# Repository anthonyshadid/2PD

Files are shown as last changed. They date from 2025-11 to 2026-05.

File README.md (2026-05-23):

# 2PD Generator

Tools for generating 3D-printable two-point discrimination wheels. Available as a web app and a native iOS app.

---

## Website

A Flask web app deployed via Docker on Render. Users can download preset STL wheels or enter 8 custom distances to generate a wheel on the server using OpenSCAD.

**Live at:** [https://anthonyshadid.github.io/2PD](https://anthonyshadid.github.io/2PD)

### How It Works

1. User enters 8 distances (0-17 mm) in the browser.
2. The server runs OpenSCAD with those distances as parameters against `discriminator.scad`.
3. The generated STL is returned as a file download.

Preset STL files (fine and broad) are served directly as static assets.

### Stack

- Python / Flask
- OpenSCAD (headless, via `xvfb-run` in the container)
- Docker, deployed on Render

### Running Locally

```bash
pip install -r requirements.txt
python app.py
```

The app starts on port 5000 by default. OpenSCAD must be installed and on your PATH.

### Running with Docker

```bash
docker build -t 2pd .
docker run -p 5000:5000 2pd
```

### Project Structure

```
app.py               Flask routes
make_wheel.py        Calls OpenSCAD to produce STL output
discriminator.scad   Parametric wheel model
templates/           HTML templates
static/presets/      Pre-built STL files
Dockerfile
render.yaml
```

### Deployment

The app deploys automatically on push to main via `render.yaml`. No manual steps needed.

---

## iPhone App

A native iOS app that generates STL files entirely on-device, no server or OpenSCAD required. The geometry is reimplemented in Swift using the same parameters as `discriminator.scad`.

**App Store:** [2PD on the App Store](https://apps.apple.com/us/app/2pd/id6761318358)

### How It Works

1. User enters up to 8 distances in the app.
2. `SCADCompatModeler.swift` computes the wheel geometry and writes an STL file.
3. The standard iOS share sheet lets the user save to Files, AirDrop, or open in a slicer app.

All processing is on-device. No network connection needed.

### Stack

- Swift / SwiftUI
- Xcode
- No third-party dependencies

### Project Structure

```
2PDiPhone/
  2PDiPhone/
    TwoPDApp.swift          App entry point, tab structure
    ContentView.swift       Distance input form and STL export
    AboutView.swift         About and usage information
    SCADCompatModeler.swift On-device STL geometry engine
    Assets.xcassets/        App icon and colors
  2PDiPhone.xcodeproj/
```

### Building

Open `2PDiPhone/2PDiPhone.xcodeproj` in Xcode and run on a simulator or device. No additional setup required.

### Modeler Parameters

The on-device modeler matches the SCAD defaults:

| Parameter | Value |
|---|---|
| Wheel diameter (flat-to-flat) | 40 mm |
| Body thickness | 3 mm |
| Prong length | 7 mm |
| Prong thickness | 1.4 mm |
| Hub diameter | 17 mm |
| Lanyard hole | 3.5 mm diameter, at corner |

---

## Contributing

Bug reports and pull requests welcome. The SCAD file and the Swift modeler should stay in sync; if you change `discriminator.scad` geometry, update `SCADCompatModeler.swift` to match.

## Authors

Anthony Shadid and Keyvon Rashidi

## License

Open source. See LICENSE for details.

## Disclaimer

Not for diagnostic use unless validated and approved by your institution. Provided as-is without warranties of any kind.

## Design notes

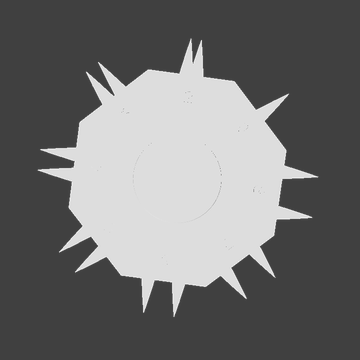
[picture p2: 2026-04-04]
static/2pd_spin.png

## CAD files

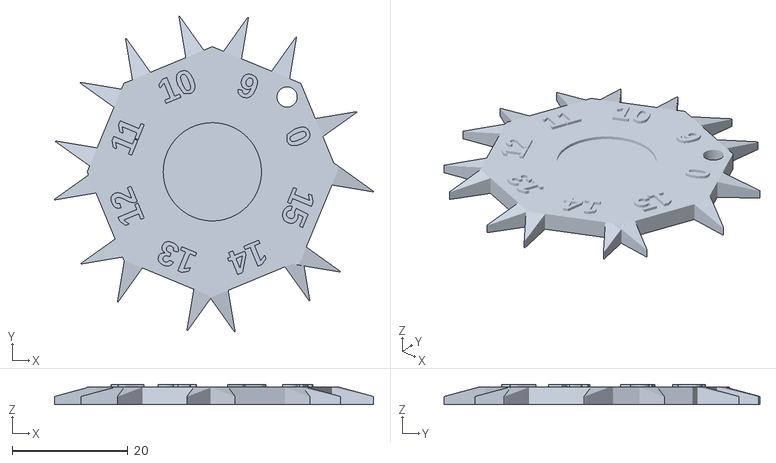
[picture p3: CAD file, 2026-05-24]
static/presets/attachables/broad_preset6 keyhole.stl
55.2 x 54.6 x 3.49

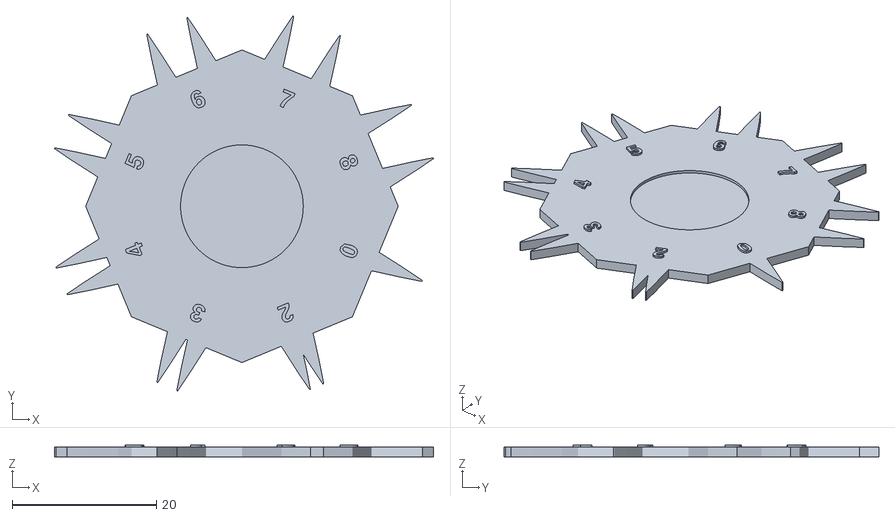
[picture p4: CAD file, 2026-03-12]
static/presets/fine_preset3.stl
52.5 x 51.9 x 1.69

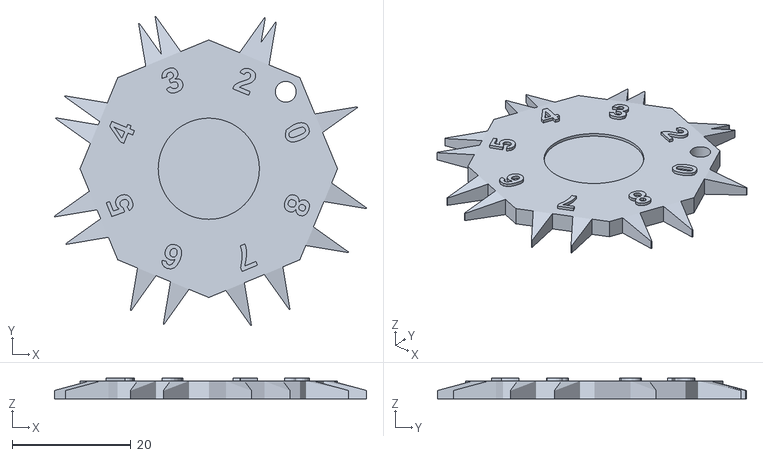
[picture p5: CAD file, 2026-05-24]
static/presets/attachables/fine_preset6 keyhole.stl
52.5 x 51.9 x 3.49

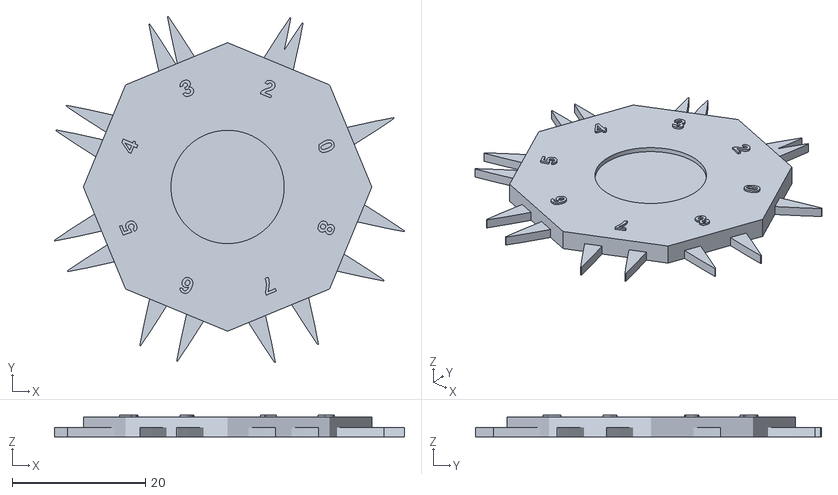
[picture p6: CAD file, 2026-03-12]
static/presets/fine_preset4.stl
52.5 x 51.9 x 3.29

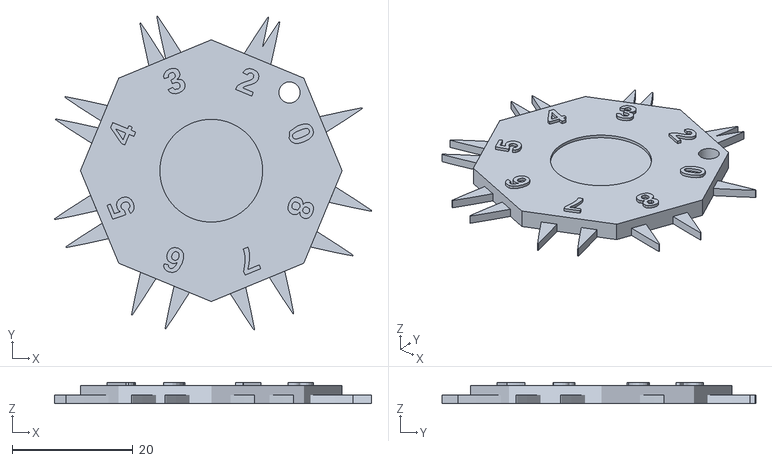
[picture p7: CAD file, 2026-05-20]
static/presets/attachables/fine_preset5 keyhole.stl
52.5 x 51.9 x 3.49

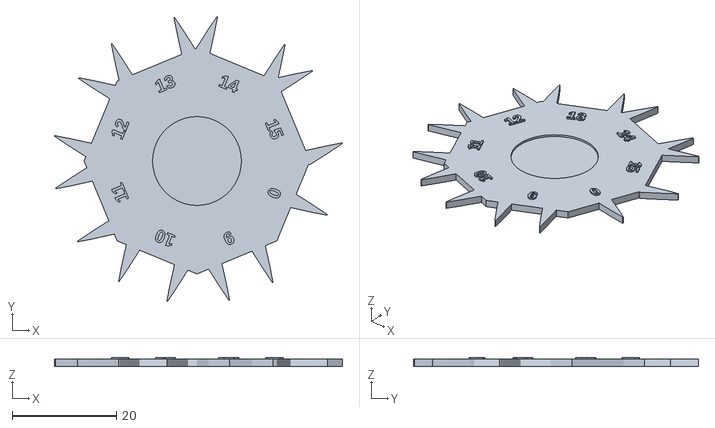
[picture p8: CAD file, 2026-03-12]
static/presets/broad_preset3.stl
55.2 x 54.6 x 1.69

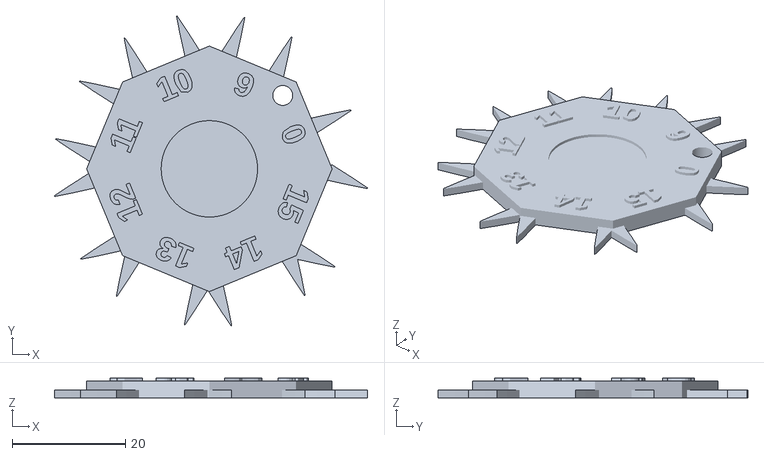
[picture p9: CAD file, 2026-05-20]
static/presets/attachables/broad_preset5 keyhole.stl
55.2 x 54.6 x 3.49

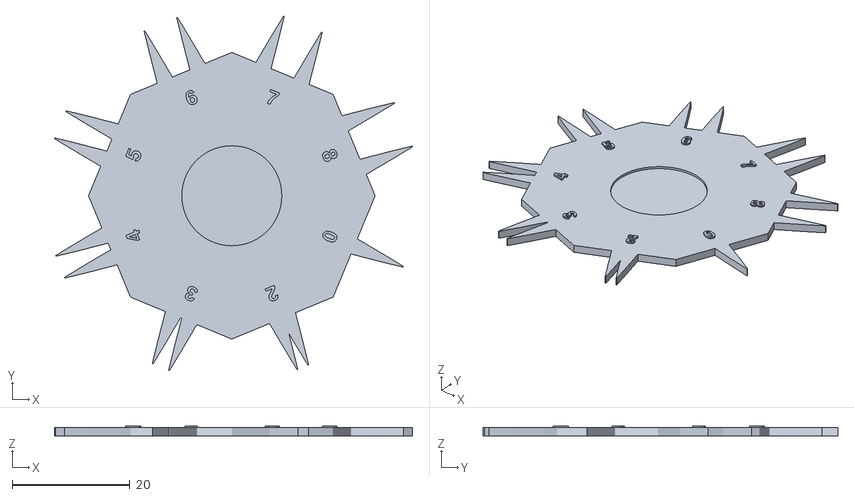
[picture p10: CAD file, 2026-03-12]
static/presets/fine_preset2.stl
60.8 x 60.3 x 1.69

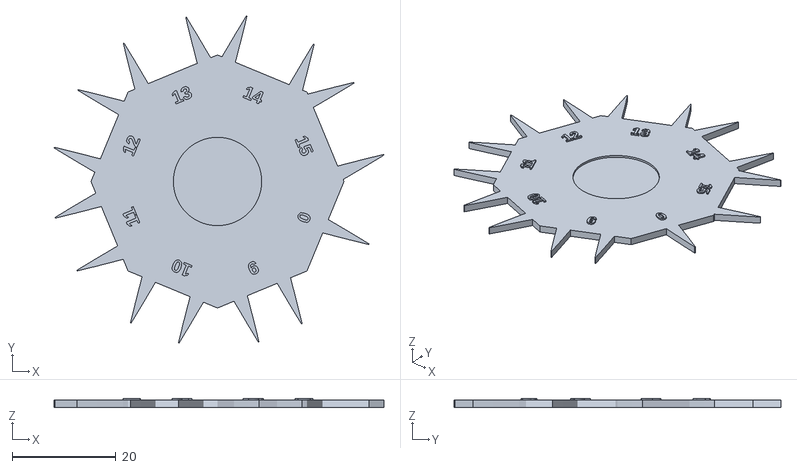
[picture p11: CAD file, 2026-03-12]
static/presets/broad_preset2.stl
63.5 x 62.9 x 1.69

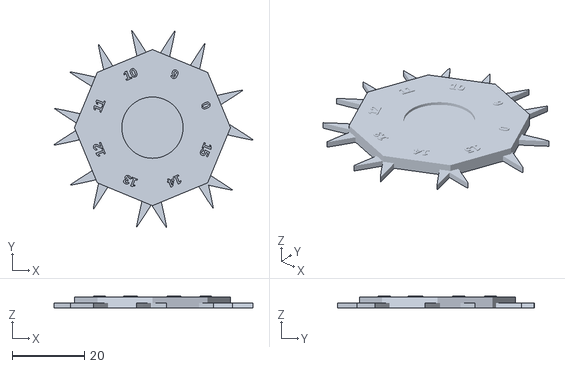
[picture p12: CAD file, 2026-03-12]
static/presets/broad_preset4.stl
55.2 x 54.6 x 3.29

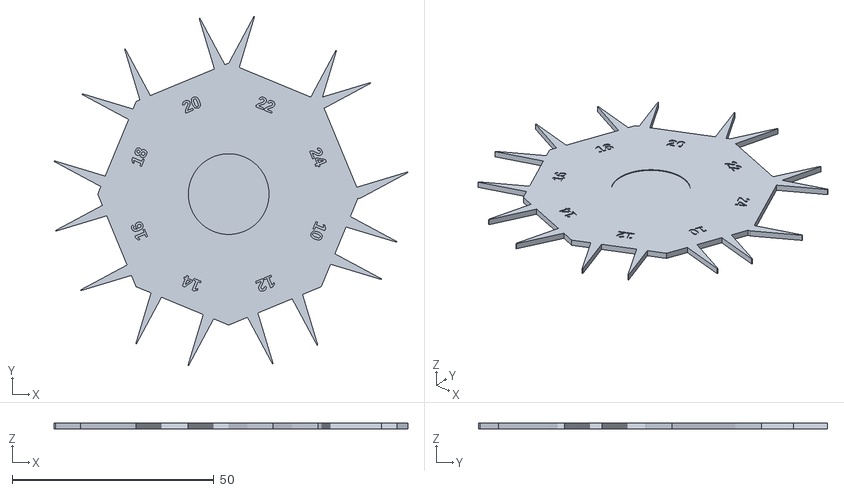
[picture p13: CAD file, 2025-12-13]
static/presets/broad_preset.stl
87.7 x 86.5 x 1.50

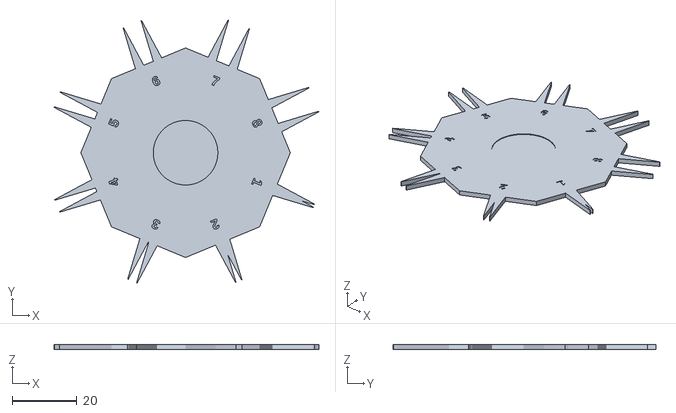
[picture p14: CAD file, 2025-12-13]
static/presets/fine_preset.stl
82.1 x 81.6 x 1.50

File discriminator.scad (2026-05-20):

// 2-Point Discrimination Wheel — parametric n-gon, COUNTERclockwise order + split thickness
// Includes badge/lanyard through-hole between 0 mm and 2 mm

distances_mm       = is_undef(distances_mm) ? [0,2,3,4,5,6,7,8] : distances_mm;

// --- geometry ---
outer_flat_to_flat = is_undef(outer_flat_to_flat) ? 40 : outer_flat_to_flat;
body_thickness     = is_undef(body_thickness) ? 3 : body_thickness;
prong_thickness    = is_undef(prong_thickness) ? 1.4 : prong_thickness;

spike_length  = is_undef(spike_length) ? 7 : spike_length;
base_d        = is_undef(base_d) ? 3 : base_d;
shank_d       = is_undef(shank_d) ? 1.4 : shank_d;
tip_d         = is_undef(tip_d) ? 0.15 : tip_d;
root_overlap  = is_undef(root_overlap) ? .7 : root_overlap;

// --- labels / hub ---
label_size    = is_undef(label_size) ? 4.3 : label_size;
label_depth   = is_undef(label_depth) ? .5 : label_depth;
font_name     = is_undef(font_name) ? "Liberation Sans:style=Bold" : font_name;
label_radial  = is_undef(label_radial) ? 0.80 : label_radial;
hub_diameter  = is_undef(hub_diameter) ? 17 : hub_diameter;
thumb_depth   = is_undef(thumb_depth) ? .5 : thumb_depth;

// --- lanyard / badge hole ---
lanyard_hole_d      = is_undef(lanyard_hole_d) ? 3.5 : lanyard_hole_d;
lanyard_hole_inset  = is_undef(lanyard_hole_inset) ? 3.35 : lanyard_hole_inset;
// larger inset = farther inward from the octagon corner
// 5.0 should place it slightly inside the corner between 0 and 2 mm

// optional
chamfer = is_undef(chamfer) ? 0.8 : chamfer;
$fn = is_undef($fn) ? 72 : $fn;

function apothem(across_flats,n)=across_flats/2;
function circ_radius(across_flats,n)=across_flats/(2*cos(180/n));

// Use BODY thickness for anything “top referenced”
function total_thickness()=body_thickness + max(chamfer,0);

module polygon_plate(n, across_flats, thk){
  r = circ_radius(across_flats,n);
  linear_extrude(thk)
    polygon(points=[for(i=[0:n-1]) let(a=360*i/n)[r*cos(a), r*sin(a)]]);
}

module spike_single_flat(len=spike_length,bd=base_d,sd=shank_d,td=tip_d){
  base_r=bd/2; shank_r=sd/2; tip_r=td/2;
  bx=-root_overlap; sx=len*0.55; tx=len;

  linear_extrude(height=prong_thickness)
  union(){
    translate([bx,0]) circle(r=base_r);
    hull(){
      translate([bx,0]) circle(r=base_r);
      translate([sx,0]) circle(r=shank_r);
    }
    hull(){
      translate([sx,0]) circle(r=shank_r);
      translate([tx,0]) circle(r=tip_r);
    }
  }
}

module thumb_well_top(){
  translate([0,0,body_thickness - thumb_depth])
    cylinder(h=thumb_depth,d=hub_diameter,$fn=72);
}

module lanyard_corner_hole(distances){
  n = len(distances);
  R = circ_radius(outer_flat_to_flat,n);

  // For default [0,2,3,4,5,6,7,8]:
  // distance[0] is at 22.5 degrees, distance[1] is at 67.5 degrees,
  // so the corner between 0 and 2 mm is at 45 degrees.
  ang = 360 / n;

  translate([(R - lanyard_hole_inset) * cos(ang),
             (R - lanyard_hole_inset) * sin(ang),
             -0.1])
    cylinder(h = body_thickness + 0.2, d = lanyard_hole_d, $fn = 72);
}

module edge_numbers_top(distances,a){
  n=len(distances);
  for(i=[0:n-1]){
    angN=+360*(i+0.5)/n;

    translate([(label_radial*a)*cos(angN),
               (label_radial*a)*sin(angN),
               body_thickness - 0.01])
      rotate([0,0,angN-90])
        linear_extrude(height=label_depth)
          text(str(distances[i]),
               size=label_size,font=font_name,
               halign="center",valign="center");
  }
}

module wheel_solid(distances){
  n=len(distances);
  a=apothem(outer_flat_to_flat,n);

  union(){
    polygon_plate(n,outer_flat_to_flat,body_thickness);

    for(i=[0:n-1]){
      angN=+360*(i+0.5)/n;

      translate([a*cos(angN),a*sin(angN),0])
        rotate([0,0,angN]){
          sep=distances[i];
          translate([0,+sep/2,0]) spike_single_flat();
          translate([0,-sep/2,0]) spike_single_flat();
        }
    }
  }
}

module discriminator(distances){
  n=len(distances);
  assert(n>=3,"distances_mm must have at least 3 entries.");

  union(){
    difference(){
      wheel_solid(distances);
      thumb_well_top();
      lanyard_corner_hole(distances);
    }

    edge_numbers_top(distances, apothem(outer_flat_to_flat,n));
  }
}
discriminator(distances_mm);

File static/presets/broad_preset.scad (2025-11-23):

// 2-Point Discrimination Wheel — parametric n-gon, clockwise order
distances_mm       = is_undef(distances_mm) ? [5,8,10,12,15,20,25,30] : distances_mm;
outer_flat_to_flat = is_undef(outer_flat_to_flat) ? 63.5 : outer_flat_to_flat;
base_thickness     = is_undef(base_thickness) ? 3.0 : base_thickness;
spike_length  = is_undef(spike_length) ? 14 : spike_length;
base_d        = is_undef(base_d) ? 3 : base_d;
shank_d       = is_undef(shank_d) ? 1.4 : shank_d;
tip_d         = is_undef(tip_d) ? 0.6 : tip_d;
root_overlap  = is_undef(root_overlap) ? 0.7 : root_overlap;
label_size    = is_undef(label_size) ? 3 : label_size;
label_depth   = is_undef(label_depth) ? 0.5 : label_depth;
font_name     = is_undef(font_name) ? "DejaVu Sans:style=Bold" : font_name;
label_radial  = is_undef(label_radial) ? 0.80 : label_radial;
hub_diameter  = is_undef(hub_diameter) ? 20 : hub_diameter;
thumb_depth   = is_undef(thumb_depth) ? 0.5 : thumb_depth;
chamfer = is_undef(chamfer) ? 0.8 : chamfer;
$fn = is_undef($fn) ? 72 : $fn;

module soft_chamfer(h=chamfer){
  if (h>0) minkowski(){ children(); cylinder(h=h,r1=h,r2=0,$fn=24); }
  else children();
}
function apothem(across_flats,n)=across_flats/2;
function circ_radius(across_flats,n)=across_flats/(2*cos(180/n));
function total_thickness()=base_thickness+max(chamfer,0);

module polygon_plate(n, across_flats, thk){
  r=circ_radius(across_flats,n);
  soft_chamfer()
    linear_extrude(thk)
      polygon(points=[for(i=[0:n-1]) let(a=360*i/n)[r*cos(a),r*sin(a)]]);
}

module spike_single_flat(len=spike_length,bd=base_d,sd=shank_d,td=tip_d){
  base_r=bd/2; shank_r=sd/2; tip_r=td/2;
  bx=-root_overlap; sx=len*0.55; tx=len;
  linear_extrude(height=base_thickness)
  union(){
    translate([bx,0]) circle(r=base_r);
    hull(){translate([bx,0])circle(r=base_r);translate([sx,0])circle(r=shank_r);}
    hull(){translate([sx,0])circle(r=shank_r);translate([tx,0])circle(r=tip_r);}
  }
}

module thumb_well_top(){
  translate([0,0,total_thickness()-thumb_depth])
    cylinder(h=thumb_depth,d=hub_diameter,$fn=72);
}

module edge_numbers_top(distances,a){
  n=len(distances);
  for(i=[0:n-1]){
    angN=-360*(i+0.5)/n;
    translate([(label_radial*a)*cos(angN),
               (label_radial*a)*sin(angN),
               total_thickness()-label_depth])
      rotate([0,0,angN-90])
        linear_extrude(height=label_depth)
          text(str(distances[i]),
               size=label_size,font=font_name,
               halign="center",valign="center");
  }
}

module wheel_solid(distances){
  n=len(distances);
  a=apothem(outer_flat_to_flat,n);
  union(){
    polygon_plate(n,outer_flat_to_flat,base_thickness);
    for(i=[0:n-1]){
      angN=-360*(i+0.5)/n;
      translate([a*cos(angN),a*sin(angN),0])
        rotate([0,0,angN]){
          sep=distances[i];
          translate([0,+sep/2,0])spike_single_flat();
          translate([0,-sep/2,0])spike_single_flat();
        }
    }
  }
}

module discriminator(distances){
  n=len(distances);
  assert(n>=3,"distances_mm must have at least 3 entries.");
  difference(){
    wheel_solid(distances);
    thumb_well_top();
    edge_numbers_top(distances,apothem(outer_flat_to_flat,n));
  }
}

discriminator(distances_mm);

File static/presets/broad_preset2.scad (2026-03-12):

// 2-Point Discrimination Wheel — parametric n-gon, clockwise order
distances_mm       = is_undef(distances_mm) ? [0,9,10,11,12,13,14,15] : distances_mm;
outer_flat_to_flat = is_undef(outer_flat_to_flat) ? 45 : outer_flat_to_flat;
base_thickness     = is_undef(base_thickness) ? 1.4 : base_thickness;
spike_length  = is_undef(spike_length) ? 9 : spike_length;
base_d        = is_undef(base_d) ? 3 : base_d;
shank_d       = is_undef(shank_d) ? 1.4 : shank_d;
tip_d         = is_undef(tip_d) ? 0.15 : tip_d;
root_overlap  = is_undef(root_overlap) ? .7 : root_overlap;
label_size    = is_undef(label_size) ? 2.5 : label_size;
label_depth   = is_undef(label_depth) ? .3 : label_depth;
font_name     = is_undef(font_name) ? "DejaVu Sans:style=Bold" : font_name;
label_radial  = is_undef(label_radial) ? 0.80 : label_radial;
hub_diameter  = is_undef(hub_diameter) ? 17 : hub_diameter;
thumb_depth   = is_undef(thumb_depth) ? 1.2 : thumb_depth;
chamfer = is_undef(chamfer) ? 0.8 : chamfer;
$fn = is_undef($fn) ? 72 : $fn;

module soft_chamfer(h=chamfer){
  if (h>0) minkowski(){ children(); cylinder(h=h,r1=h,r2=0,$fn=24); }
  else children();
}
function apothem(across_flats,n)=across_flats/2;
function circ_radius(across_flats,n)=across_flats/(2*cos(180/n));
function total_thickness()=base_thickness+max(chamfer,0);

module polygon_plate(n, across_flats, thk){
  r = circ_radius(across_flats,n);
  linear_extrude(thk)
    polygon(points=[for(i=[0:n-1]) let(a=360*i/n)[r*cos(a), r*sin(a)]]);
}


module spike_single_flat(len=spike_length,bd=base_d,sd=shank_d,td=tip_d){
  base_r=bd/2; shank_r=sd/2; tip_r=td/2;
  bx=-root_overlap; sx=len*0.55; tx=len;
  linear_extrude(height=base_thickness)
  union(){
    translate([bx,0]) circle(r=base_r);
    hull(){translate([bx,0])circle(r=base_r);translate([sx,0])circle(r=shank_r);}
    hull(){translate([sx,0])circle(r=shank_r);translate([tx,0])circle(r=tip_r);}
  }
}

module thumb_well_top(){
  translate([0,0,total_thickness()-thumb_depth])
    cylinder(h=thumb_depth,d=hub_diameter,$fn=72);
}

module edge_numbers_top(distances,a){
  n=len(distances);
  for(i=[0:n-1]){
    angN=-360*(i+0.5)/n;
    translate([(label_radial*a)*cos(angN),
               (label_radial*a)*sin(angN),
               base_thickness - 0.01])
      rotate([0,0,angN-90])
        linear_extrude(height=label_depth)
          text(str(distances[i]),
               size=label_size,font=font_name,
               halign="center",valign="center");
  }
}


module wheel_solid(distances){
  n=len(distances);
  a=apothem(outer_flat_to_flat,n);
  union(){
    polygon_plate(n,outer_flat_to_flat,base_thickness);
    for(i=[0:n-1]){
      angN=-360*(i+0.5)/n;
      translate([a*cos(angN),a*sin(angN),0])
        rotate([0,0,angN]){
          sep=distances[i];
          translate([0,+sep/2,0])spike_single_flat();
          translate([0,-sep/2,0])spike_single_flat();
        }
    }
  }
}

module discriminator(distances){
  n=len(distances);
  assert(n>=3,"distances_mm must have at least 3 entries.");

  union(){
    difference(){
      wheel_solid(distances);
      thumb_well_top();
    }
    edge_numbers_top(distances, apothem(outer_flat_to_flat,n));
  }
}
discriminator(distances_mm);

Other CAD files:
static/presets/broad_preset3.scad
static/presets/attachables/broad_preset5 keyhole.scad
static/presets/attachables/broad_preset6 keyhole.scad
static/presets/attachables/fine_preset6 keyhole.scad
static/presets/broad_preset4.scad
static/presets/fine_preset.scad
static/presets/fine_preset2.scad
static/presets/fine_preset3.scad
static/presets/fine_preset4.scad
static/presets/standard_preset.scad

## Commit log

2025-11-10 Sync local project with GitHub repo
    [discriminator.scad, wheel.stl, wheel_1-3-5-7-9-11-13-15_20251109-161019.stl]
2025-11-10 Updated: smooth conical teeth correctly aligned
    [discriminator.scad]
2025-11-10 Added Through Cut Numbers
2025-11-12 flat model
    [discriminator.scad]
2025-12-13 new model
    [discriminator.scad]
2025-12-13 thin 2PD
    [broad_preset.stl, fine_preset.stl, standard_preset.stl]
2025-12-13 cleanupgit status
    [discriminator.scad]
2026-05-20 Fix custom STL generation and preset links
    [broad_preset5 keyhole.stl, fine_preset5 keyhole.stl]
2026-05-20 Update custom SCAD model
    [discriminator.scad]
2026-05-20 Update preset5 label geometry
    [broad_preset5 keyhole.scad, broad_preset5 keyhole.stl, fine_preset5 keyhole.scad, fine_preset5 keyhole.stl]
2026-05-20 Update custom label geometry
    [discriminator.scad]
2026-05-23 Rework UI and update STL modeler geometry
    ContentView: remove dev-only quick-test button, add per-field mm unit
    labels, show filled-count footer, disable Generate until ≥3 fields are
    filled, use icon label on the generate button.
    AboutView: rewrite with InfoSection component, fix parameter table to
    match current modeler (outer_flat_to_flat=40, prong=1.4 mm, etc.),
    remove placeholder/AI-generated copy, clean contributors list.
    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
2026-05-23 Fix 0mm validation and add keyboard Done button
2026-05-23 Fix non-manifold body geometry: correct top face, hole normals, pocket
2026-05-24 Add tapered preset6 prongs
    [broad_preset6 keyhole.scad, broad_preset6 keyhole.stl, fine_preset6 keyhole.scad, fine_preset6 keyhole.stl]
